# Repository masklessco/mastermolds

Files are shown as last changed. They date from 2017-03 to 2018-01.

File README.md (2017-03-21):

# Master Molds
A collection of master mold CAD files from the [maskless.co](http://maskless.co) community. These molds can be used to make PDMS microfluidic devices without the need for a cleanroom.

# Instructions
Choose an example or template to start from, modify to your needs, then head over to [maskless.co](http://maskless.co) to [place your order](https://shop.trycelery.com/page/58bde872bcc8c012009c42f1). Detailed instructions can be found [here](https://github.com/masklessco/mastermolds/blob/master/instructions/README.md).

Get 20% off when you share your design! Enter coupon code 'sharealike', and we will upload your design file to our public GitHub repository with a CC-BY-SA license.

# License
All designs in this repository are licensed [CC-BY-SA 3.0] (https://creativecommons.org/licenses/by-sa/3.0/)

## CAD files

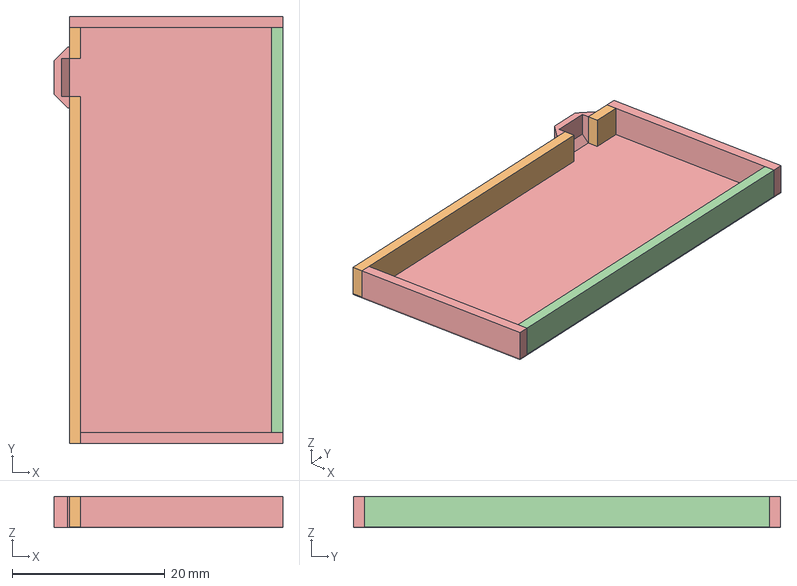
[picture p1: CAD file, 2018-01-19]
templates/medium mold templates/Maskless_Medium_WithWalls_FreeCAD_Template_v2.FCStd
30.0 x 56.0 x 4.12 mm
Base and Walls - do not edit

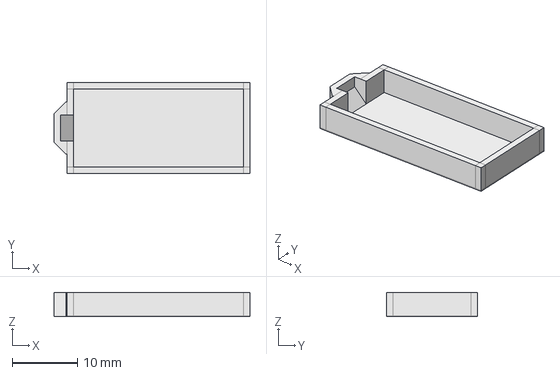
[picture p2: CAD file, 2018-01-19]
templates/small mold templates/Maskless_Small_WithWalls_FreeCAD_EmptyTemplate_v4.FCStd
30.0 x 14.0 x 3.73 mm

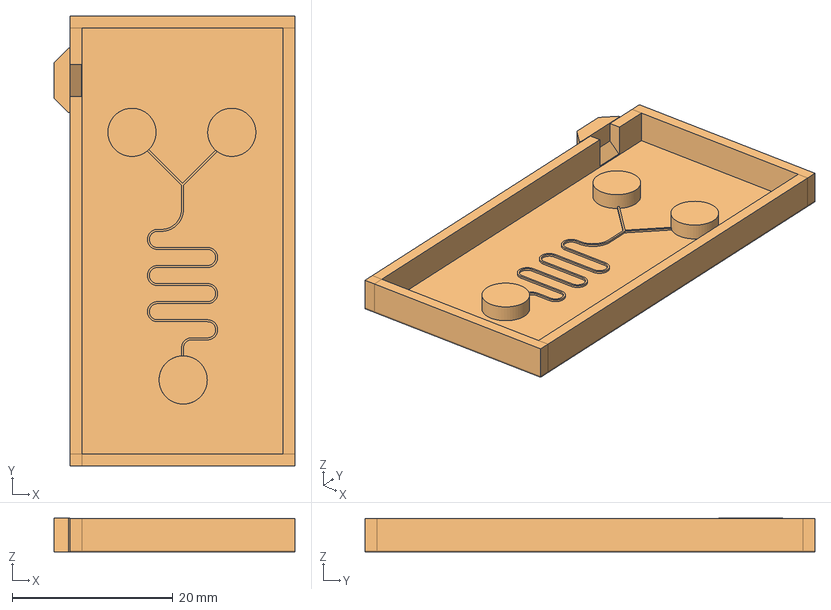
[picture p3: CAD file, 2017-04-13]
templates/medium mold templates/Maskless_Medium_WithWalls_FreeCAD_ExampleA_v1.FCStd
30.0 x 56.0 x 4.20 mm

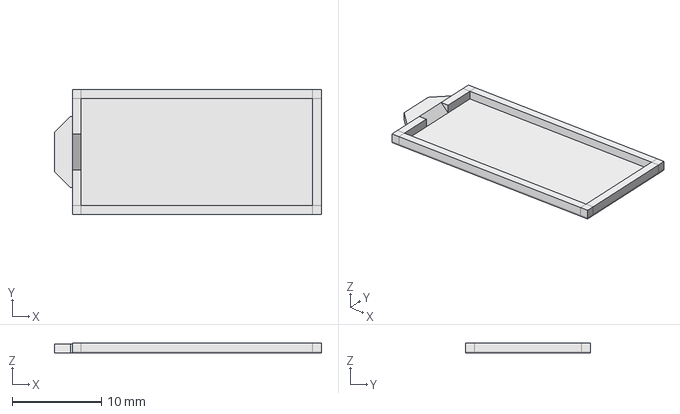
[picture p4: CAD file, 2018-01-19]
templates/small mold templates/Maskless_Small_WithWalls_FreeCAD_EmptyTemplate_v6.FCStd
30.0 x 14.0 x 1.12 mm

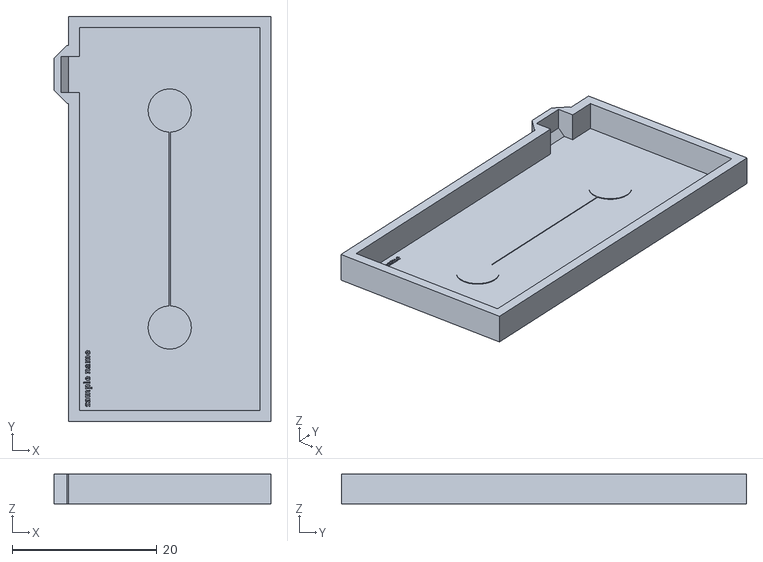
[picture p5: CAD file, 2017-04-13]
templates/medium mold templates/Maskless_Medium_WithWalls_FreeCAD_Template_v1.stl
30.0 x 56.0 x 4.12

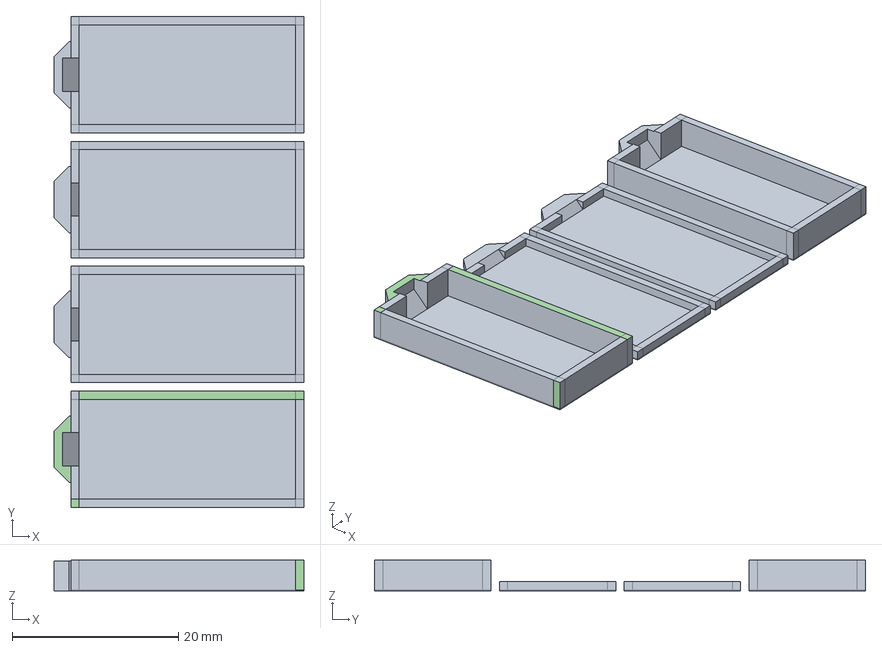
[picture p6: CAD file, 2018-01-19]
templates/small mold templates/Maskless_Small_WithWalls_FreeCAD_EmptyTemplate_v5.FCStd
30.0 x 59.0 x 3.73 mm
Base
Walls
Base001
Walls001
Base002
Walls002
Base003
Walls003

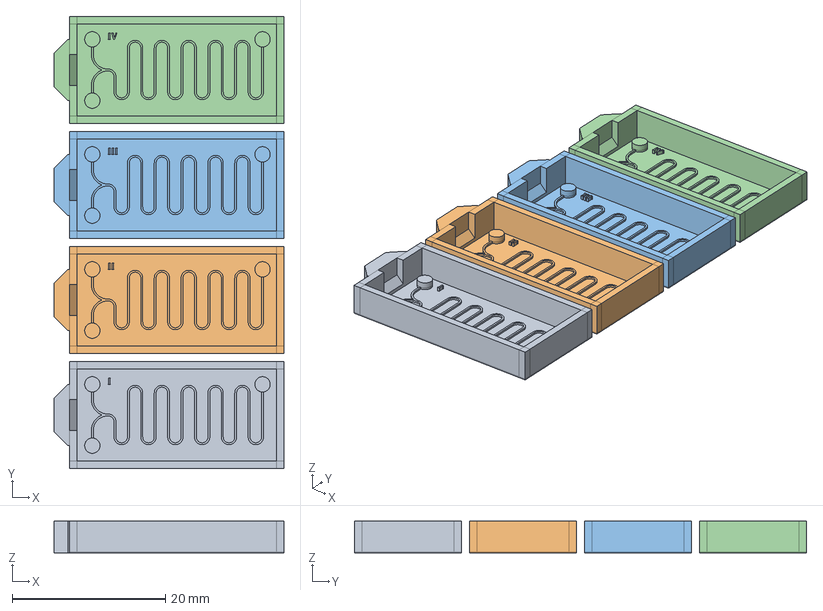
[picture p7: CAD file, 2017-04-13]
templates/small mold templates/Maskless_Small_WithWalls_FreeCAD_ExampleC_v1.FCStd
30.0 x 59.0 x 4.12 mm

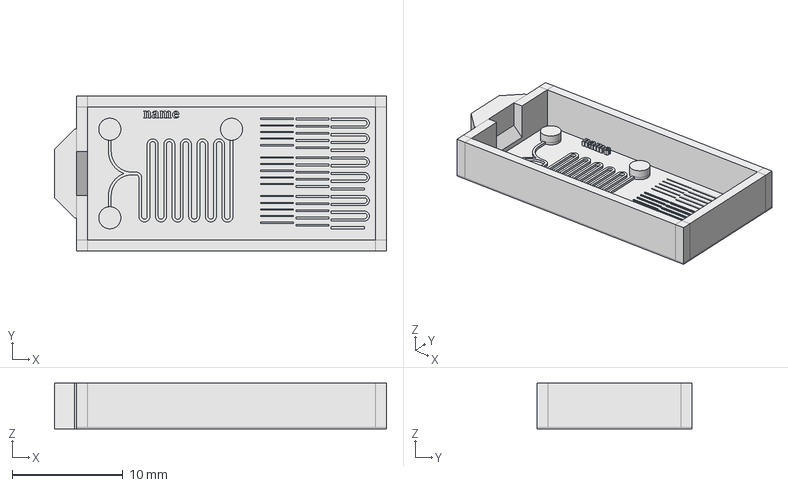
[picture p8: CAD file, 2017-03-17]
templates/small mold templates/Maskless_Small_WithWalls_FreeCAD_ExampleB_v2.FCStd
30.0 x 14.0 x 4.12 mm

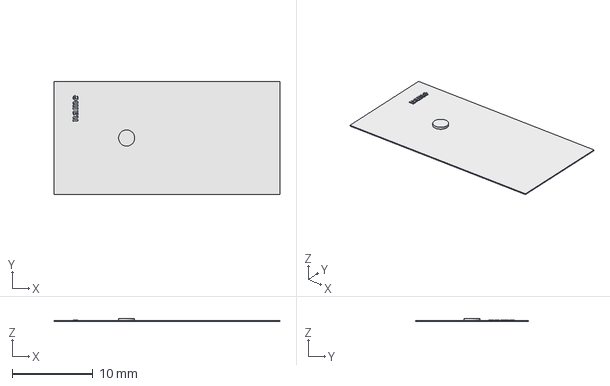
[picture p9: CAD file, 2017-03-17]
templates/small mold templates/Maskless_Small_NoWalls_FreeCAD_EmptyTemplate_v1.FCStd
28.0 x 14.0 x 0.425 mm

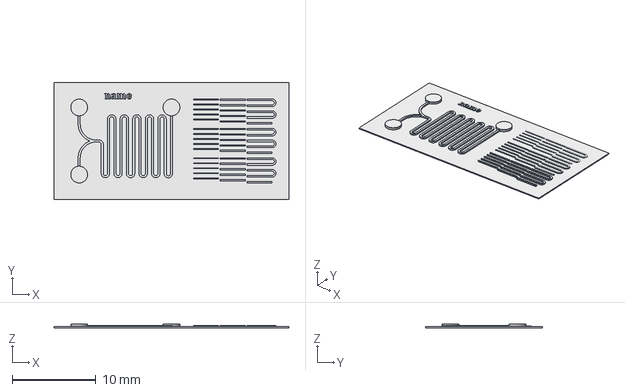
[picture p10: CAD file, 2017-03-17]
templates/small mold templates/Maskless_Small_NoWalls_FreeCAD_ExampleA_v1.FCStd
28.0 x 14.0 x 0.425 mm

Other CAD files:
templates/small mold templates/Maskless_Small_WithWalls_AutoCAD_EmptyTemplate_v1.stl
templates/small mold templates/Maskless_Small_WithWalls_FreeCAD_EmptyTemplate_v3.FCStd
templates/medium mold templates/Maskless_Medium_WithWalls_FreeCAD_ExampleA_v1.stl
templates/medium mold templates/Maskless_Medium_WithWalls_FreeCAD_Template_v2.stl
templates/small mold templates/Maskless_Small_NoWalls_FreeCAD_EmptyTemplate_v1.stl
templates/small mold templates/Maskless_Small_NoWalls_FreeCAD_ExampleA_v1.stl
templates/small mold templates/Maskless_Small_WithWalls_AutoCAD_EmptyTemplate_v1.dwg
templates/small mold templates/Maskless_Small_WithWalls_FreeCAD_EmptyTemplate_v3.stl
templates/small mold templates/Maskless_Small_WithWalls_FreeCAD_EmptyTemplate_v4.stl
templates/small mold templates/Maskless_Small_WithWalls_FreeCAD_EmptyTemplate_v5.stl
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

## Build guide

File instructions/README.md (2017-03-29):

# Design your device

Head over to the templates folder to download the mold template of your choice. Design your microfluidic master mold. Be sure to follow our suggeted [design guidelines] (https://github.com/masklessco/mastermolds/blob/master/instructions/Maskless_Design_Rules_Tolerances_v1.mdown). Email your design to molds@maskless.co and [place your order](https://shop.trycelery.com/page/58bde872bcc8c012009c42f1). Your design will be treated as confidential unless you use the 'sharealike' coupon code, in which case we will upload your CAD file to this repository.

# What's in the Box

1.	Mold(s) of large or small size, with or without walls
2.	Glass substrate: molds are printed onto a glass substrate. This substrate can be easily removed or kept for convenient handling. If the mold delaminates from the glass, it can be glued back on or arranged and glued onto a different substrate, if desired.

# PDMS Casting Instructions

 1.	Remove Maskless mold from packaging. Place mold in a petri dish or aluminum foil dish to prevent spilling of PDMS throughout the process below.  
 2.	Dry mold at 80 ºC for 30 to 60 minutes prior to first use. Allow mold to return to room temperature.
 3.	Prepare PDMS precursor according to desired protocol. A recommended procedure is as follows:
 a)	Weigh Sylgard 184 parts A and B in a 10:1 ratio by weight and mix thoroughly.
 b)	Degass the PDMS precursor under vacuum until all visible bubbles disappear.
 4.	For molds with walls: pour the PDMS precursor into the mold. The volume of PDMS precursor may be weighed in order to keep the thickness of the device consistent: use up to 0.9 mL for the small sized molds and up to 4 mL for the large sized molds. For molds without walls, place mold in a plastic or aluminum foil petri dish and pour PDMS on top of the mold.
 5.	Degass the PDMS for a second time in the mold.
 6.	Cure the PDMS in the mold. Oven curing at 80 ºC for 15 – 40 minutes is recommended. Remove the mold from heat and allow to cool to room temperature.
 7.	Use a flat tweezer or other small, flat edge to dislodge PDMS from mold on one end of the mold. Use the tweezers to pull the PDMS out of the mold.
 8.	Finish processing the PDMS replica by treating the surface (such as with reactive ion etching), adhering to glass, and inserting tubing according to desired procedure.
 9.	Mold can be reused without additional treatment. If needed, mold can be rinsed with water or isopropyl alcohol and dried at 80 ºC, taking care not to abrade the fine features in the mold.

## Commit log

2017-03-06 Initial small mold templates
    [Maskless_Small_WithWalls_FreeCAD_Template_v2.FCStd, Maskless_Small_WithWalls_FreeCAD_Template_v2.stl]
2017-03-06 Create Master Mold Intructions.md
2017-03-07 fix folders
    [Maskless_Small_WithWalls_FreeCAD_Template_v2.FCStd, Maskless_Small_WithWalls_FreeCAD_Template_v2.stl]
2017-03-16 Edited printable area
    Fixed typo on "area".
    Changed printable area to that of small mold, taking into account area that will actually print accurately.
2017-03-17 Templates added
    Added small mold templates with and without molds, including empty
    templates and example molds.
    [Maskless_Small_NoWalls_FreeCAD_EmptyTemplate_v1.FCStd, Maskless_Small_NoWalls_FreeCAD_EmptyTemplate_v1.stl, Maskless_Small_NoWalls_FreeCAD_ExampleA_v1.FCStd, M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]
2017-03-24 Added tolerances requested by Paul Lum
    Added tolerances based on 3D confocal microscope images and to address
    Paul’s questions
2017-03-24 Minor edit
    Changed “printable area” to “printable design area”
2017-03-24 Deleted redundant files
    the open office and pdf versions of these don’t need to be publicly
    available on GitHub… I still have the files, but we can just use the
    markdown file that is still on GitHub
2017-03-24 Minor edit
    Under point 4, changed “weighed” to “measured”
2017-03-24 Minor edit
    What I original called “large” molds are actually going to be “medium”
    sized molds.
2017-03-25 AutoCAD template
    Added AutoCAD template for small walled mold and corresponding stl
    [Maskless_Small_WithWalls_AutoCAD_EmptyTemplate_v1.dwg, Maskless_Small_WithWalls_AutoCAD_EmptyTemplate_v1.stl]
2017-04-13 Added medium FreeCAD templates
    Started adding medium mold templates here.
    [Maskless_Medium_WithWalls_FreeCAD_ExampleA_v1.FCStd, Maskless_Medium_WithWalls_FreeCAD_ExampleA_v1.stl, Maskless_Medium_WithWalls_FreeCAD_Template_v1.FCStd, Ma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]
2017-04-14 Included medium mold design area
    added 48 mm x 24 mm total design area for medium molds.
2018-01-19 Adjusted tolerances
    Changed tolerances roughly based on what is easy to print without many
    iterations (can be improved in the future when we can better predict)
    [Maskless_Medium_WithWalls_FreeCAD_Template_v2.FCStd, Maskless_Medium_WithWalls_FreeCAD_Template_v2.stl, Maskless_Small_WithWalls_FreeCAD_EmptyTemplate_v4.FCStd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]
